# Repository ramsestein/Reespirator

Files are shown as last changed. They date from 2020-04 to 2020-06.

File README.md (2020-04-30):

# Reespirator 2020

Este repositorio pretende documentar y organizar los pasos para fabricar prototipos de  **Reespirator-2020**, un respirador open-source basado en el sistema de ventilación mecánica Jackson-Rees, diseñado y mejorado a partir de los prototipos elaborados por el equipo de Reesistencia Team para todas aquellas personas, organizaciones o empresas que quieran fabricarlo en cualquier parte del mundo.  

> ESTA DOCUMENTACIÓN ESTÁ EN ELABORACIÓN, COMPRUEBE REGULARMENTE LOS CAMBIOS, LAS PRIMERAS VERSIONES PUBLICADAS ESTÁN DESACTUALIZADAS. 

## Disclaimer
*Recuerde que un respirador es un dispositivo médico que sólo puede ser utilizado por personal cualificado y que un mal respirador o un respirador mal utilizado puede matar.*

La presente documentación **NO PERMITE CONSTRUIR UN RESPIRADOR FINAL**, sólo se publica para que se pueda fabricar PROTOTIPOS para investigación. 

## Info
*¿Qué es Reespirator 2020?*

El dispositivo Reespirator 2020 es un prototipo de sistema respirador de emergencia con elementos disponibles por la mayoría de las personas en cualquier parte del mundo, de rápida construcción y con la capacidad para mantener constantes ventilatorias aceptables en un paciente afecto de [Síndrome de Distrés Respiratorio Agudo](https://es.wikipedia.org/wiki/S%C3%ADndrome_de_dificultad_respiratoria_aguda) o SDRA que esperamos puede ser aplicable a los pacientes con COVID-19.

Aunque el origen de Reespirator es España, debido a las regulaciones y validaciones necesarias para los productos médicos, y aunque Reespirator 23 de [Reesistencia Team](https://gitlab.com/reesistencia), en el que se basó inicialmente este nuevo diseño, ha superado varias pruebas preclínicas con animales, y de compatibilidad electromagnética, suponemos que este dispositivo nunca se llegará a fabricar masivamente en España, dónde afortunadamente lo peor de la crisis del COVID-19 parece que ya ha pasado (08/04/20); esperamos que este y otros diseños puedan ser útiles en otros países.

Aún así no nos damos por vencidos y seguiremos desarrollando el proyecto al menos en 2 versiones:

* Versión low cost (basada en Arduino y con caja de metacrilato, madera...)
* Versión pro (con un autómata PLC + un HMI y caja de chapa plegada en acero inoxidable)

En la siguiente figura podemos ver una representación del dispositivo:

Reespirator

## Primeros pasos
**Antes de montar un respirador lea toda la documentación posible e infórmese bien, si necesita alguna aclaración abra un Issue y lo corregiremos en cuanto podamos. Si cree que puede mejorar el diseño, el código o que falta alguna cosa importante envíenos un Pull Request.**

## [Información médica básica del dispositivo Reespirator 2020](https://gitlab.com/reespirator/reespirator2020/-/blob/master/medical/MEDICAL.md)
El dispositivo se está diseñando para intentar cumplir las siguientes [especificaciones clínicas](https://foro.coronavirusmakers.org/index.php?p=/discussion/44/especificaciones-clinicas-de-un-respirador-util-en-esta-crisis#latest). Los dispositivos que estamos prototipando podrán funcionar en diferentes modos ventilatorios. En el siguiente enlace tendrás acceso a [Información médica básica sobre el dispositivo Reespirator 2020](https://gitlab.com/reespirator/reespirator2020/-/blob/master/medical/MEDICAL.md)

## [Estructura básica](https://gitlab.com/reespirator/reespirator2020/-/blob/master/case/CASE.md)
La versión low-cost de Reespirator 2020 consta de una [caja](https://gitlab.com/reespirator/reespirator2020/-/blob/master/case/CASE.md) diseñada para fabricarse mediante corte láser que contiene casi todos elementos del respirador en su interior. En el prototipo actual las piezas del prototipo se han diseñado para su corte por láser en metacrilato, si bien la imagen anterior corresponde a la nueva evolución que podrá fabricarse también con chapa plegada.

## [Sistema neumático](https://gitlab.com/reespirator/reespirator2020/-/blob/master/neumatic/NEUMATIC.md)
El [sistema neumático](https://gitlab.com/reespirator/reespirator2020/-/blob/master/neumatic/NEUMATIC.md) del Reespirator 2020 está basado en un sistema Jackson-Rees. Reespirator 2020 utiliza además una serie de válvulas, sensores de presión y caudal y tubuladuras para hacer llegar al aire a los pulmones del paciente.

## [Mecánica](https://gitlab.com/reespirator/reespirator2020/-/blob/master/mechanic/MECHANIC.md)
El [sistema mecánico](https://gitlab.com/reespirator/reespirator-doc/-/blob/master/mechanic/MECHANIC.md) pretende realizar los movimientos necesarios para realizar las maniobras de inspiración y espiración forzada del paciente mediante elementos mecánicos sustituyendo al personal humano que utilizaría el sistema de ventilación.

## [Electrónica](https://gitlab.com/reespirator/reespirator2020/-/blob/master/electronics/ELECTRONICS.md)
La [electrónica](https://gitlab.com/reespirator/reespirator-doc/-/blob/master/electronics/ELECTRONICS.md) de control gestiona el movimiento del motor y los sensores que permiten realizar un control de lazo cerrado automatizado del sistema.
Además de la electrónica de control se emplea una electrónica adicional como interfaz de usuario que permite monitorizar diferentes señales del respirador y modificar en tiempo real diferentes configuraciones del mismo.

## [Firmware](https://gitlab.com/reespirator/reespirator-doc/-/blob/master/firmware/FIRMWARE.md)
El sistema de control necesita ser programado con un [firmware](https://gitlab.com/reespirator/reespirator-doc/-/blob/master/firmware/FIRMWARE.md) que permita hacer funcionar el dispositivo. Dicho programa se ha realizado conforme a las especificaciones de los especialistas médicos para realizar las funciones para las que el dispositivo fue diseñado.

## [Simulación](https://gitlab.com/reespirator/reespirator2020/-/blob/master/simulation/SIMULATION.md)
En este apartado se consideran los fundamentos del sistema de control en lazo cerrado para los distintos modos de control que permite el Reespirator 2020. Los modelos matemáticos que permiten la [simulación numérica](https://gitlab.com/reespirasistemator/reespirator2020/-/blob/master/simulation/SIMULATION.md) del comportamiento del sistema corresponden a la información de este apartado.

## [Lista de materiales](https://gitlab.com/reespirator/reespirator2020/-/blob/master/bom/BOM.md)
La [lista de materiales, (BOM o Bill of materials)](https://gitlab.com/reespirator/reespirator2020/-/blob/master/bom/BOM.md) para construir un Reespirator 2020 es cuando menos complicada, incluye elementos como metacrilato, madera, MDF o chapa para la caja, sistmeas electrónicos como un Arduino Mega o un autómata PLC, y otros componentes, pero también elementos mecánicos y otros incluso impresos en 3D; pero sobre todo requiere también de la utilización de sistemas médicos tales como tubuladuras y un sistema ventilatorio Jackson-Rees.

## [Manual de usuario](https://gitlab.com/reespirator/reespirator2020/-/blob/master/manual/MANUAL.md)
El dispositivo Reespirator 2020 es un dispositivo médico y su uso sólo debe realizarse por personal especializado. Ofrecemos aquí un breve [manual de uso](https://gitlab.com/reespirator/reespirator-doc/-/blob/master/manual/MANUAL.md) del mismo; pero es el personal sanitario el que sabe los parámetros que deben utilizarse para el tratamiento de un paciente.

## [Vídeos]
En el siguiente enlace podemos ver algunos vídeos con detalles del Reespirator 2020 en funcionamiento:

* https://www.youtube.com/channel/UC9xr1HbWGLBjd4ADTvGcOnw

## Historia y principales cambios de esta versión

El proyecto Reespirator2020 toma como punto de partida el proyecto Reespirator 23 (o 24) v3 de **Reesistencia Team** a partir del cual realizamos un fork, el repositorio original está en [https://gitlab.com/reesistencia](https://gitlab.com/reesistencia).

En esta nueva versión se incluyen principalmente los siguientes cambios:

 - Revisión y reestructuración en profundidad del códido de Arduino para asegurar la robustez de funcionamiento en todos los supuestos.
 - La recuperación del interfaz básico con LCD de 20x04 y elementos sencillos de control (4 pulsadores y un encoder con pulsador).
 - Establecimiento y documentación de una interfaz de comunicación serie que permite la utilización de sistemas (en adelante llamados Display+) de visualización, control y conectividad, que pueden ser utilizados como accesorios para aportar mejor usabilidad al sistema.
 - Se trabaja para estandarizar y popularizar los sensores y electro-válvulas para utilizar partes (comerciales o diseñadas) posibles de conseguir con la situación de emergencia actual y a precios accesibles.
 - Posibilidad de usar diferentes interfaces de usuario.
 - Opción de utilizar un microcontrolador tipo Arduino o similar o bien un autómata PLC.

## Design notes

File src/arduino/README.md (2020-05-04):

# Arduino

> Estamos elaborando una nueva versión para Arduino más sólida a partir de la versión del software que se ha hecho para el PLC. En las carpetas https://gitlab.com/reespirator/firmware y https://gitlab.com/reespirator/display están las versiones de los desarrollos actuales de Reespirator 2020.

## Reespirator 23

En el repositorio https://gitlab.com/reesistencia/reespirator está el código de la versión utilizada originalmente en Reespirator 23 para Arduino y la Beagle Bone con una pantalla táctil de 7" de WaveShare.

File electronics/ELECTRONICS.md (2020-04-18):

## Electrónica
La electrónica de control gestiona el movimiento del motor y los sensores que permiten realizar un control de lazo cerrado automatizado del sistema. Además se emplea una electrónica adicional de interfaz de usuario que permite monitorizar diferentes señales del respirador y modificar en tiempo real diferentes configuraciones del mismo.

* En la versión de [Arduino](https://gitlab.com/reespirator/reespirator2020/-/blob/master/electronics/arduino/ARDUINO-ELECTRONICS.md) la electrónica de control está basada en un Arduino Mega y una serie de dispositivos sensores y actuadores conectados al mismo para realizar un sistema de control en lazo cerrado. 

* Estamos trabajando también en una versión basada en un autómata o [PLC](https://gitlab.com/reespirator/reespirator2020/-/blob/master/electronics/PLC/PLC-ELECTRONICS.md) que fundamentalmente ha permitido realizar una correcta modelización del sistema.

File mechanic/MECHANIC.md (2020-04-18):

El sistema mecánico de Reespirator utiliza un motor Nema 23/24 que hace oscilar una leva con forma de caracol y esta mueve a su vez una palanca que bascula haciendo moverse al empujador que aprieta sobre el globo del Jackson-Rees.

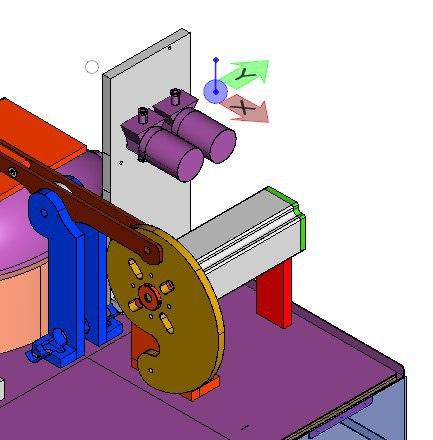
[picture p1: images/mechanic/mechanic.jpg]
Detalle Detalle de la leva, el motor y la palanca


La parte mecánica consta de:

* Una leva fabricada en metacrilato de 8mm. con un casquillo adaptador, fabricado en acero o aluminio.

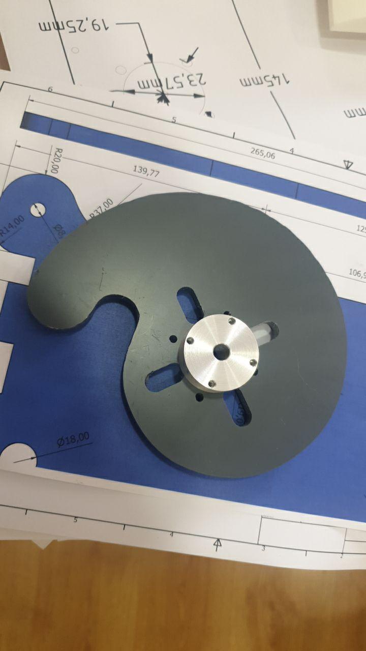
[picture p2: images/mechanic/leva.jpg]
Leva Leva cortada en madera


* Un balancín formado por 2 piezas de metacrilato de 4 mm. Dispone de un rodamiento 608ZZ, que entra en contacto con la leva y pivota sobre un tornillo M8 que lo ancla a la estructura de la caja, y en su parte final está fijado a una pala, impresa en 3D, con dos tornillos M5.

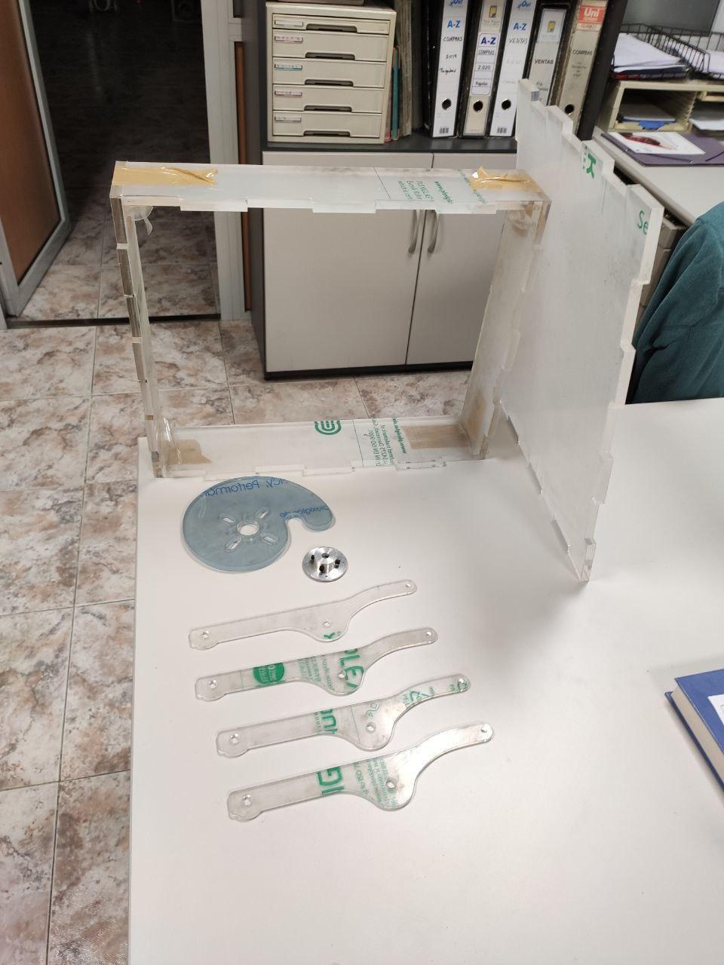
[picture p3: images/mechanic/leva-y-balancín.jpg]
Piezas del balancín y la leva Piezas del balancín y la leva cortadas en metacrilato


* La carcasa, que contiene todo el dispositivo está fabricada en metacrilato de 10mm, dispone además de un embellecedor, cortado en láser de metacrilato de 4mm para protección mecánica.

Caja cortada por láser

* Además, dispone de una [cuna](https://gitlab.com/reespirator/reespirator2020/-/blob/master/files/stl/cuna.stl "Cuna impresa en 3D para alojar el balón del Jackson-Rees") impresa en 3D donde se aloja el balón respirador de Jackson Rees.

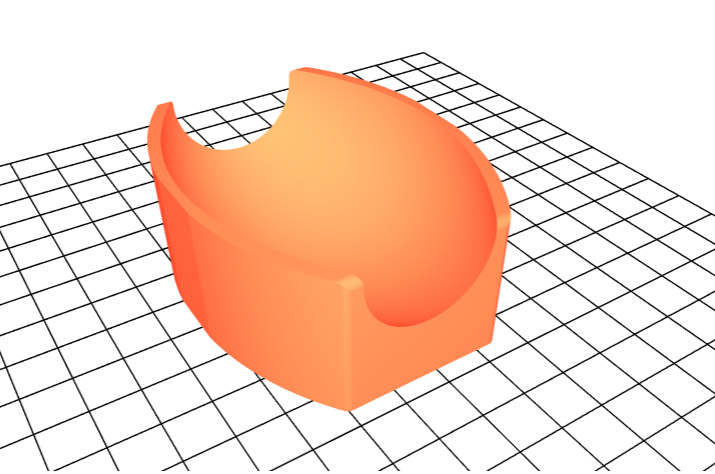
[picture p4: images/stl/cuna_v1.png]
Cuna para el Jackson-Rees


* El sistema utiiza también una [pala o empujador](https://gitlab.com/reespirator/reespirator2020/-/blob/master/files/stl/empujador_v3.stl "Cuna impresa en 3D para alojar el balón del Jackson-Rees") impresa en 3D que empuja el balón respirador para insuflar el aire al paciente. 

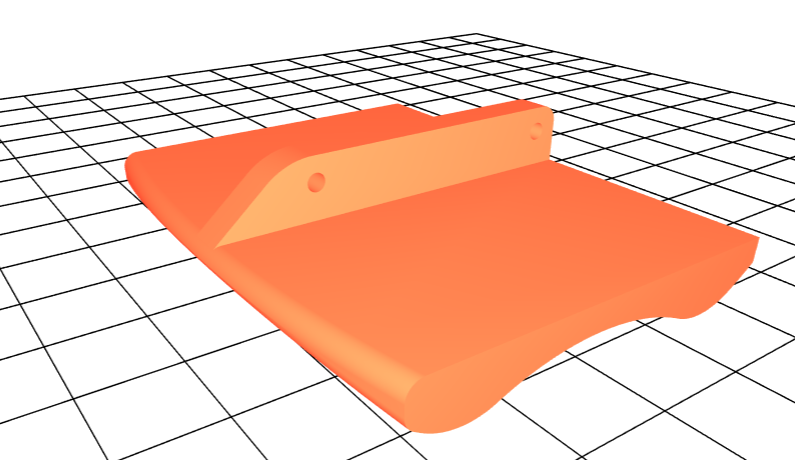
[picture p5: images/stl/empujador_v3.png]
Pala o empujador


*Estas 2 piezas se imprimirán en 3D con la mayor calidad posible, pues ambas quedan en contacto con el globo y no deben tener fallos que puedan dañar el mismo.*

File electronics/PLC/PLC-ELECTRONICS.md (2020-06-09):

***Este documento describe la electrónica basada en PLC. Si desea ver la versión para Arduino, está disponible en el siguiente enlace: https://gitlab.com/reespirator/reespirator2020/-/blob/master/ARDUINO-ELECTRONICS.md***

## Electrónica con PLC 
La electrónica de control gestiona el movimiento del motor y los sensores que permiten realizar un control de lazo cerrado automatizado del sistema. Además se emplea una electrónica adicional de interfaz de usuario que permite monitorizar diferentes señales del respirador y modificar en tiempo real diferentes configuraciones del mismo.

El diagrama de bloques funcionales y elementos electrónicos del sistema se muestra en la siguiente figura:
_PENDIENTE_

### PLC

Según este esquema podemos ver que el sistema electrónico está compuesto por un autómata SIEMENS Simatic S7-1200 CPU 1215c al que se conectan los sensores y actuadores del sistema. Opcionalmente se puede suministrar la misma CPU en su versión SAFETY CAT-IV/SIL 3 mejorando grandemente tiempo medio entre fallos (mtbf), que ya de por si es bajo.

SIEMENS Simatic S7-1200

### Display táctil

Dispone de un display táctil SIEMENS TP700, con las siguientes capacidades: registro de alarmas, histórico de datos, monitorización remota con gestión de usuario y password para evitar accionamientos no autorizados. El gestor de accesos indica en la pantalla si se está operando sobre la pantalla en remoto. Dispone de una memoria SD para almacenamiento de datos de alarmas y datos de trabajo.

SIEMENS TP700

### Etapa de alimentación:
El dispositivo está preparado para conectarse a la red eléctrica de 110-230V de corriente alterna y utiliza una fuente de alimentación principal de baja tensión de 24V de corriente continua capaz de suministrar al menos 15A. Para mantener su funcionamiento en caso de fallo de la alimentación debe emplearse un SAI o bien solicitar alimentación auxiliar de 24Vdc.

### Sistema de actuación y sensorización

* Se utilizarán motores NEMA, concretamente NEMA 24 que si bien no son tan comunes como los NEMA 23 dan un torque suficiente. En los prototipos hemos utilizado motores de 4,2N/m. En cualquier caso el uso de otro tipo de motores debe garantizar la suficiente presión sobre el globo del Jackson-Rees para producir el suficiente flujo ventilatorio.

Nema 24 Motor Nema 24

* Los motores NEMA se controlarán con un driver HSS57. Se ha elegido este modelo ya que puede controlar tanto el NEMA24 como motores más pequeños sin necesidad de cambiar todo el hardware.
En el repositorio está publicado también el driver para este modelo.

Esquema de conexión Esquema de conexión del driver y el motor paso a paso

* Para monitorizar la posición inicial del sistema, se utilizará un sensor de efecto hall o un simple final de carrera, (aunque también se ha considerado la opción de un segundo sensor para evitar problemas).

* Electroválvula de 24V para el control de salida de aire del sistema neumático, (en el prototipo original se utilizaron 2 porque eran de un diámetro demasiado pequeño como para permitir un caudal apropiado).

* Sensor de caudal Sensirion SFM3300-AW para la medición del caudal en el espacio muerto del sistema de ventilación. Al ser una pieza que estará en contacto con el circuito de inspiración del paciente, se emplea un sensor homologado para aplicaciones médicas. (Si este modelo no estuviera disponible se pueden buscar sustitutos y con pequeñas modificaciones del código se podrían utilizar igualmente).

Caudalímetro

* Sensor de presión diferencial para la diferencia de presión que existe entre el circuito inspiratorio y la presión ambiental. Se ha empleado el modelo ABPLANT001PG2A5 de Honeywell, que está homologado para aplicaciones médicas. (En versiones previas utilizamos 2 BME280 conectados por SPI).

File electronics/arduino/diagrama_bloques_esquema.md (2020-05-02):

## Diagrama Bloques Placa Electrónica Principal ##

La electrónica principal para la versión de Arduino se basa en el desarrollo de una placa PCB de doble cara diseñada para montaje SMD. Esta placa contendrá los elementos necesarios para asegurar la protección ESD así como los distintos elementos para el control de los sensores, actuadores y comunicación con el exterior.

Para aclarar cada una de las partes de las que consta esta placa, se desglosará el esquemático en los siguientes bloques que se exponen a continuación, (en los enlaces siguientes encontrarás más información):

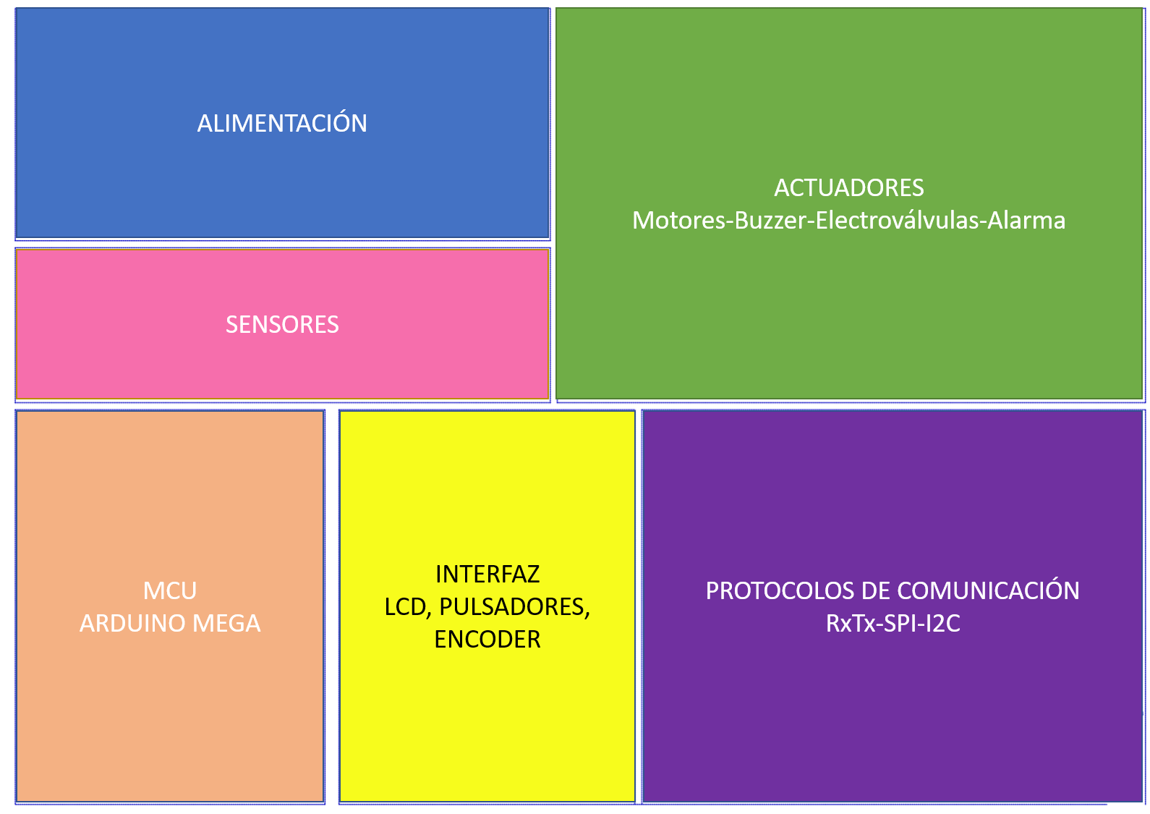
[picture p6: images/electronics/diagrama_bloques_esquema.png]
Diagrama Bloques Esquema Electrónico Diagrama de Bloques de la Electrónica


[- Alimentación.](https://gitlab.com/reespirator/reespirator2020/-/blob/master/electronics/arduino/alimentacion_esquema.md "Alimentacion Esquema")

[- Actuadores: Motores, buzzer, electroválvulas, alarma.](https://gitlab.com/reespirator/reespirator2020/-/blob/master/electronics/arduino/actuadores_esquema.md "Actuadores")

[- Sensores.](https://gitlab.com/reespirator/reespirator2020/-/blob/master/electronics/arduino/sensores_esquema.md "Sensores")

[- Interfaz: LCD, encoder, pulsadores.](https://gitlab.com/reespirator/reespirator2020/-/blob/master/electronics/arduino/interfaz_esquema.md "Interfaz")

[- Protocolos de comunicación: SPI, I2C, TxRx.](https://gitlab.com/reespirator/reespirator2020/-/blob/master/electronics/arduino/comunicacion_esquema.md "Protocolos de Comunicación")

[- MCU: Arduino Mega.](https://gitlab.com/reespirator/reespirator2020/-/blob/master/electronics/arduino/mcu_esquema.md "MCU Conexiones")

## Representación Tridimensional de la PCB ##

Como resultado de este trabajo se obtiene la siguiente PCB en la que se pude ver una representación tridimensinal:

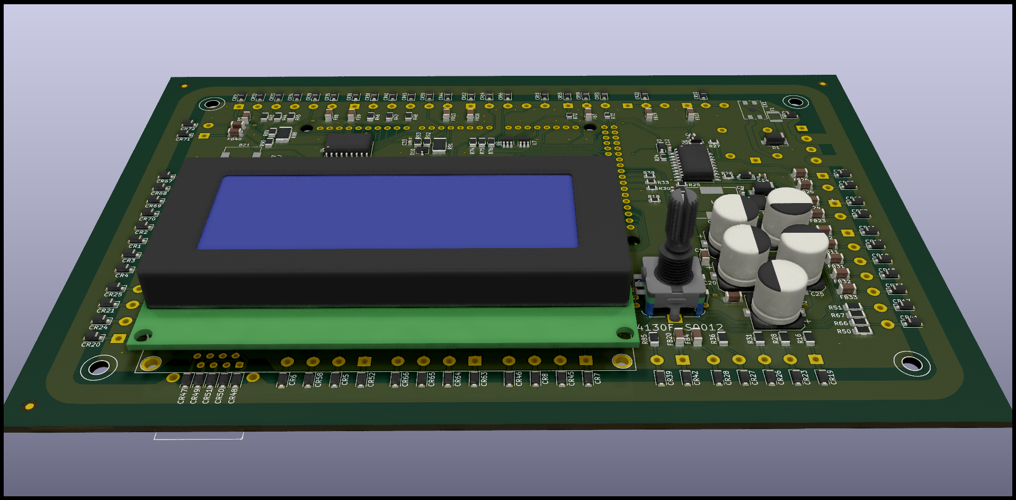
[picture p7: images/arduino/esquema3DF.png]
Representación 3D Parte Superior Representación 3D de la Electrónica. Parte superior


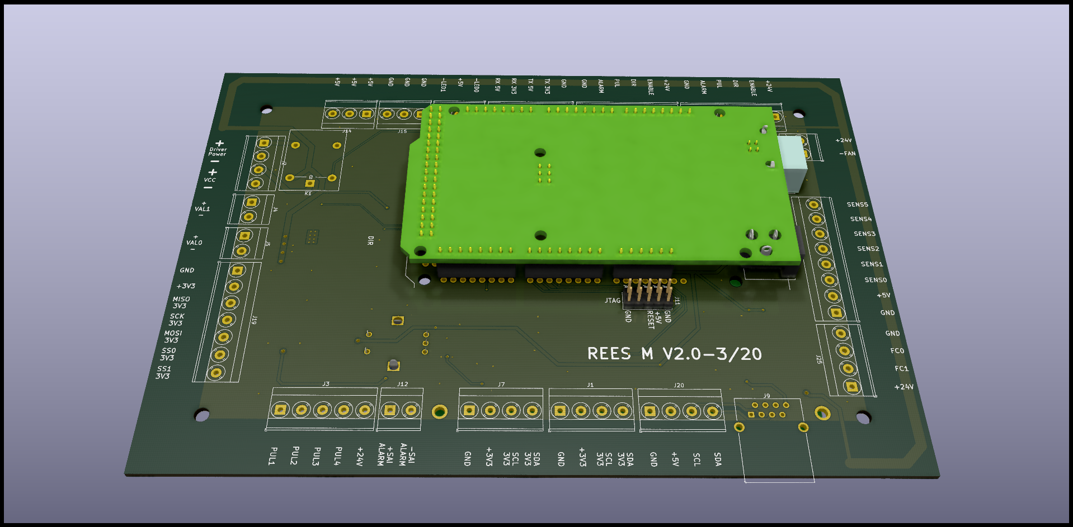
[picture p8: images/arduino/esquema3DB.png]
Representación 3D Parte Inferior Representación 3D de la Electrónica. Parte Inferior


## Diseño PCB ##

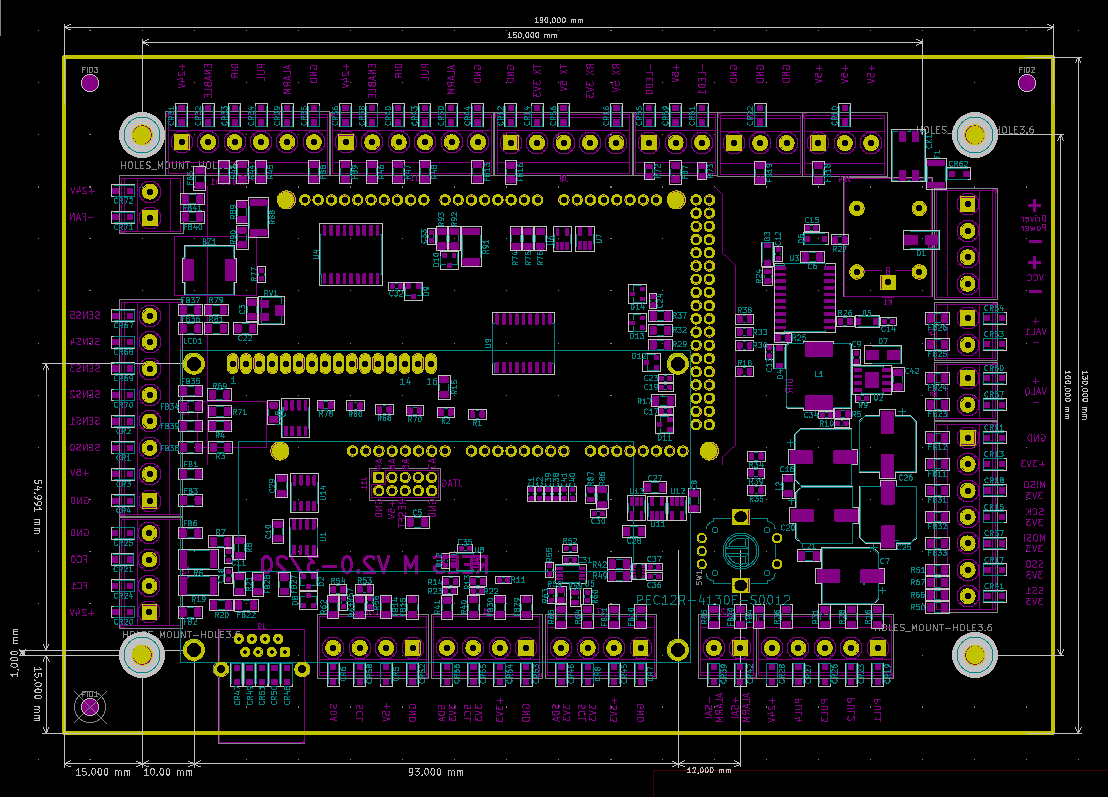
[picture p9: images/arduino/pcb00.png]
Diseño PCB Representación de pads


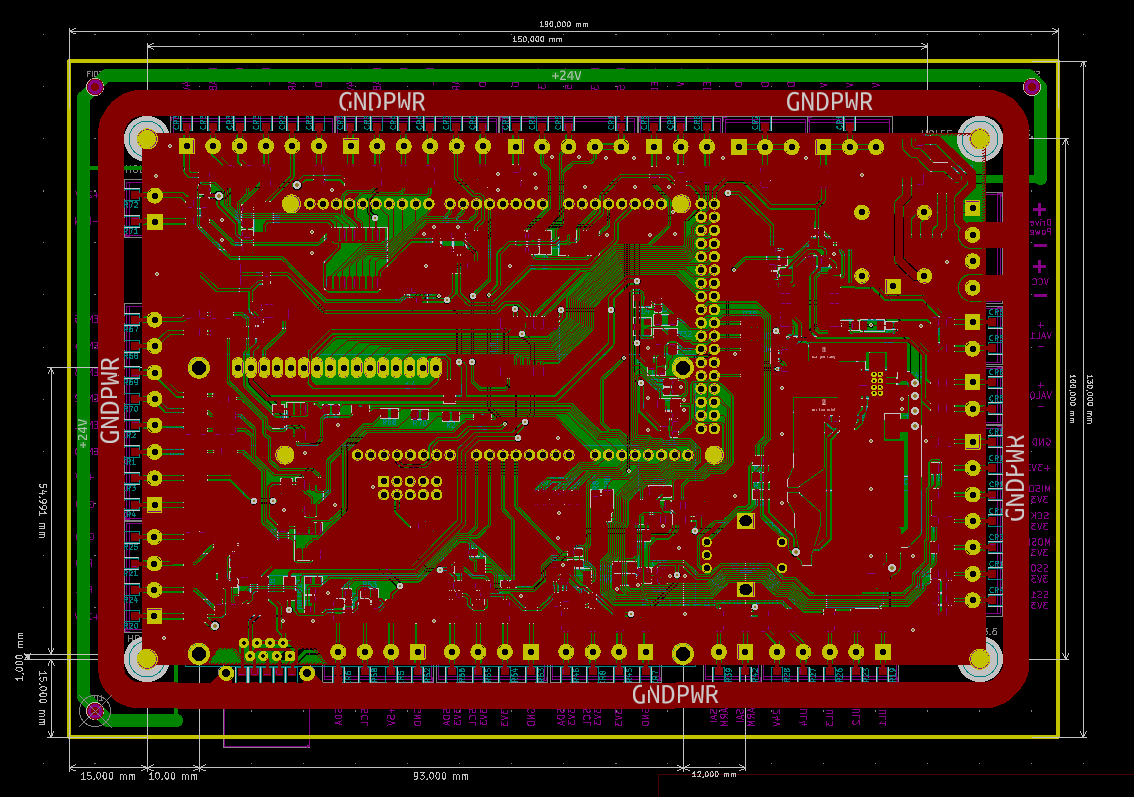
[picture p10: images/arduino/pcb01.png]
Diseño PCB PCB Completa


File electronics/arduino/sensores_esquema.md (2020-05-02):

El diagrama de bloques de la placa de circuito impreso diseñada para la versión del arduino, está disponible en el siguiente enlace:

**[Diagrama de Bloques](https://gitlab.com/reespirator/reespirator2020/-/blob/master/electronics/arduino/diagrama_bloques_esquema.md "Diagrama de Bloques")**

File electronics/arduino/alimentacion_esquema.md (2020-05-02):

## Fuente de Alimentación. ##

Para la alimentación el sistema se empleará una fuente de alimentación capaz de suministrar un mínimo de 3A y con salida de 24V.

De entre todas las fuentes del mercado, lo recomendable sería emplear una fuente que haya sido diseñada para emplearse en equipos médicos puesto que dispondrá de circuitos específicos para el aislamiento ante posibles interferencias (EMI).

Preferiblemente se optará por una fuente de alimentación conmutada que permite entre otras cosas disponer de una fuente de alimentación menos voluminosa con un mayor rendimiento.

Un posible diagrama de bloques de la fuente de alimentación seleccionada es la que se presenta en la figura siguiente:

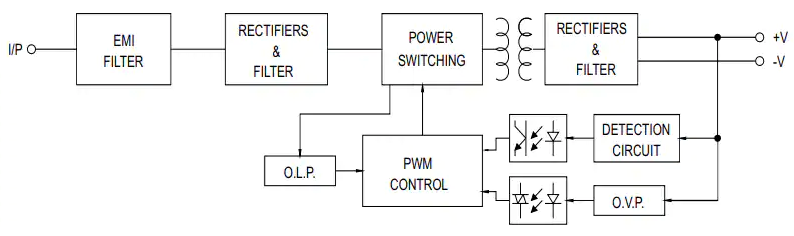
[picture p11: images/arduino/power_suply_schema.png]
Diagrama Bloques Fuente Alimentación


Existen muchas alternativas en el mercado, por lo que atendiendo a la disponibilidad y coste, se podrá optar por una u otra. Dicha fuente es la que alimentará entre otras partes del sistema a la placa de circuito impreso que se ha desarrollado. 

## Esquema del circuito electrónico de alimentación. ##

Como se podrá observar, esta parte del circuito corresponde a la alimentación de los distintos componentes y al sistema en general. Cabe destacar que se parte de una fuente de alimentación de +24V en corriente continua como se ha indicado anteriormente.

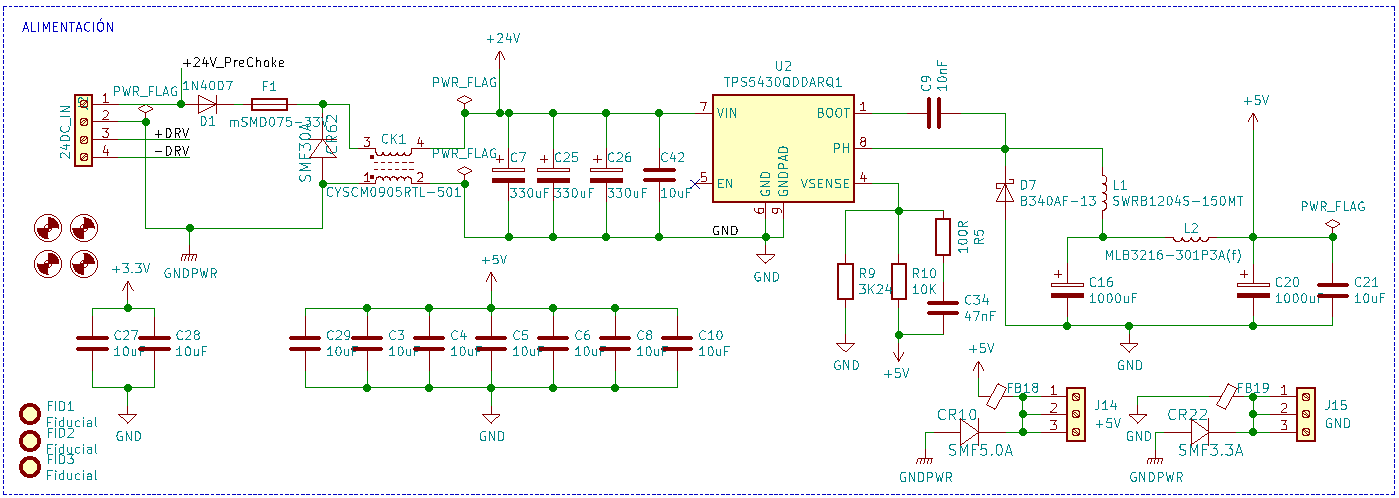
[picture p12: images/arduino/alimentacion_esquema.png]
Esquema Fuente Alimentación


En el esquema se puede observar cómo de los bornes de entrada de la fuente de alimentación de 24V tenemos 4 salidas, las dos primeras son las que proporcionarán tensión y corriente a toda la placa, mientras que las dos inferiores son las que proporcionarán tensión al DRV.

La alimentación pasa a través de F1 que servirá de fusible para proteger el sistema y tras él se encuentra un Choke para evitar las interferencias y proteger de EMI. Tras el Choke CK1, se pueden distingir dos apartados:

- El primero de ellos es una **salida de +24V**. Esta salida se empleará en la parte de actuadores como drivers, válvulas..etc., como se verá más adelante.
- La segunda es una **salida de 5V** que se obtiene tras pasar un convertidor DC/DC con capacidad para conducir 3A. 

Todo esto permite tener una alimentación estable en la placa de +24V y +5V, protegida por diferentes componentes como ferritas y diodos de protección.

En esta parte también se puede ver una red de condensadores que son de desacoplo y que estarán ubicados lo más próximos posible a la alimentación de los circuitos integrados. 
Y por último también se pueden observar algunos de los conectores  de alimentación, que estarán disponibles para conectar periféricos, todos ellos protegidos por diodos unidireccionales TVS (Transient Voltage Suppressors).

El diagrama de bloques de la placa de circuito impreso diseñada para la versión del arduino, está disponible en el siguiente enlace:

**[Diagrama de Bloques](https://gitlab.com/reespirator/reespirator2020/-/blob/master/electronics/arduino/diagrama_bloques_esquema.md "Diagrama de Bloques")**

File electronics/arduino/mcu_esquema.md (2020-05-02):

## MCU Esquema. ##

Como se ha comentado en varias ocasiones, esta versión del respirador está basada en un Arduino Mega 2560.
Este microcontrolador será el encargado de llevar a cabo el control y gestión del sistema, sin embargo, dependiendo de la versión de la interfaz escogida, podrá relegar el control de la visualización a otro sistema a parte que permita la representación gráfica.

En cualquier caso, la placa desarrollada dispone de varias opciones de visualización tal y como se ha detallado en la documentación, en el apartado: [Interfaz](https://gitlab.com/reespirator/reespirator2020/-/blob/master/electronics/arduino/interfaz_esquema.md "Interfaz") 

En la siguiente imagen se puede ver el esquema de conexión empleado en el sistema.

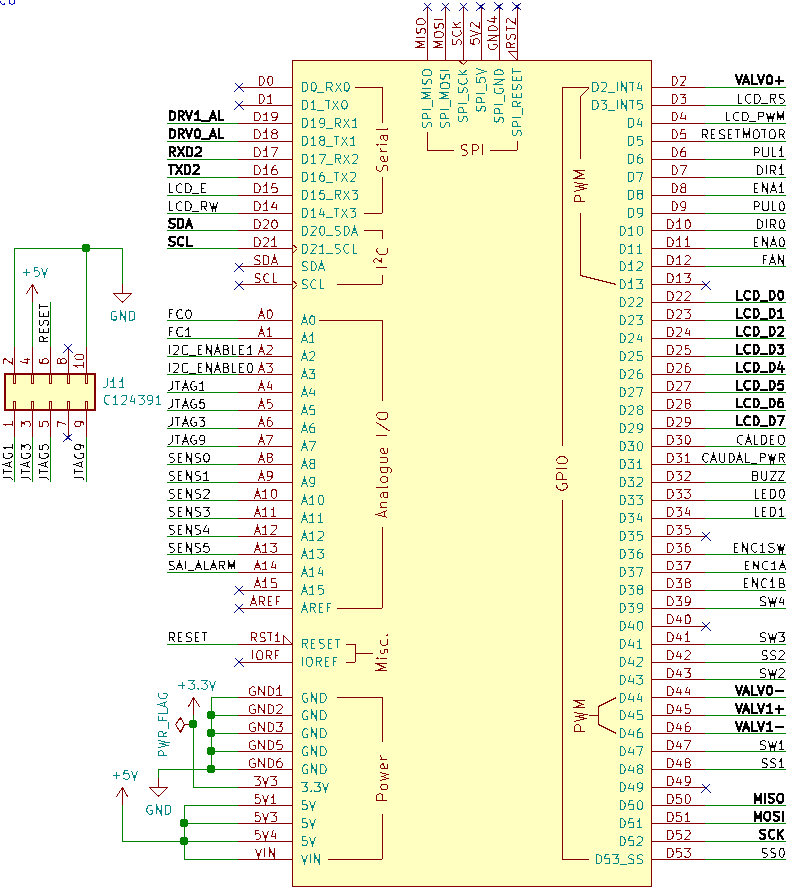
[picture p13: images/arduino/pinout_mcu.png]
MCU


Como se puede apreciar en la imagen, se dispone por un lado del microcontrolador con su pinout, donde se han señalado en **negrita**, aquellos pines fijos que no podían reubicarse en el diseño de la pcb, y por otro lado, existe un bloque denominado J11 consistente en un conector para facilitar la depuración del sistema mediante JTAG.

A partir del microcontrolador, se tiene toda la información proveniente de sensores y por lo tanto permitirá actuar sobre los distintos elementos como alarma, buzzer, válvulas..etc.

El diagrama de bloques de la placa de circuito impreso diseñada para la versión del arduino, está disponible en el siguiente enlace:

**[Diagrama de Bloques](https://gitlab.com/reespirator/reespirator2020/-/blob/master/electronics/arduino/diagrama_bloques_esquema.md "Diagrama de Bloques")**

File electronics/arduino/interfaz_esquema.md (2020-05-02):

## Interfaz del Sistema. ##

La interacción del usuario con el sistema se realizará a través de una serie de pulsadores y un encoder, además de un display, la ubicación de estos elementos estará debajo de un LCD 4x20 y a la derecha del mismo respectivamente.

Como se indicó en la introducción a la electrónica del respirador, este dispositivo **se ha pensado para tener distintas opciones de montaje y funcionamiento**, siendo la que se detalla a continuación la básica de ellas, pero no la única, puesto que **el sistema está preparado para la conexión a través de los terminales de TxRx y/o del USB**, para la comunicación con otros periféricos de visualización como puede ser una pantalla oled o HMI. 

**La selección de una forma de representación u otra se realizará vía firmware** por lo que no es necesario realizar ningún acople o adaptación a la placa desarrollada, simplemente se seleccionará el dispositivo de visualización deseado o instalado en el equipo en el firmware que se programa en el Arduino Mega.

**Esta versión de LCD 4x20, fue la primera versión que se pensó debido a su bajo coste y a la facilidad para disponer de estas en cualquier parte del mundo**, sin embargo, su limitación a la hora de representar señales y/o gráficas ha hecho necesario adaptar el sistema a otro tipo de dispositivos.

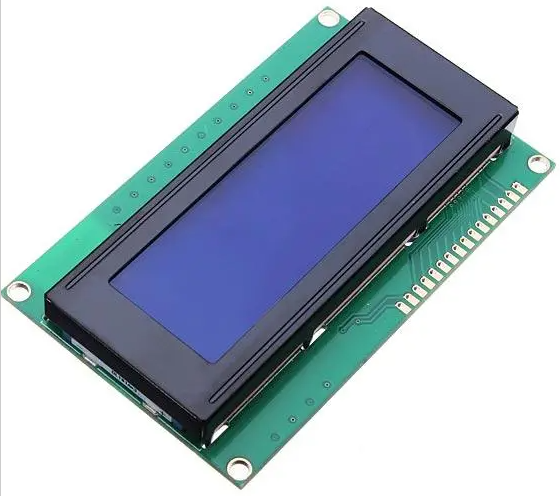
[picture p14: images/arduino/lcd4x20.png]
LCD 4x20 LCD 4X20


En la siguiente imagen se puede ver el esquema de esta parte del sistema.

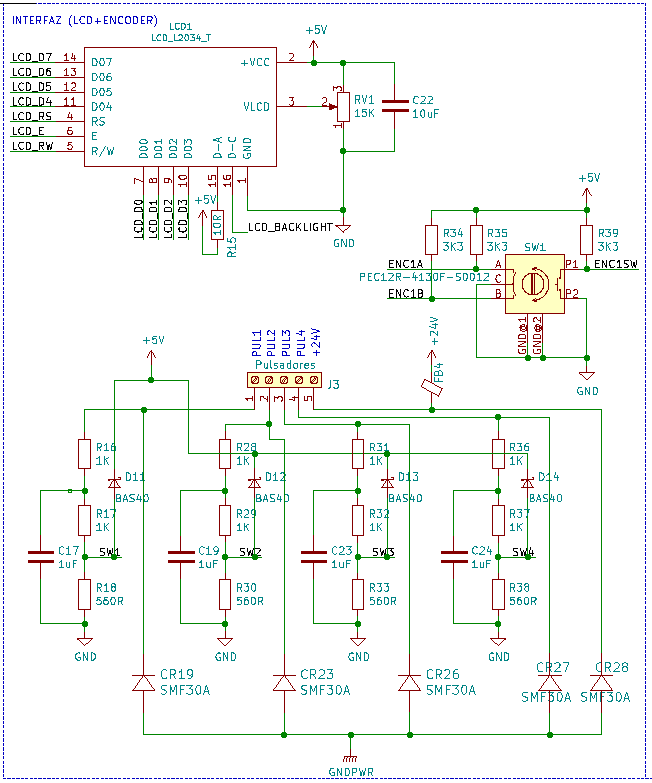
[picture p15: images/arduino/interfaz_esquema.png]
Esquema de la Interfaz


Como se puede comprobar, se dispone de un LCD con backlight el cual se encuentra conectado en paralelo con el Arduino Mega, disponiendo de un potenciómetro para regular el contraste.

En cuanto a los pulsadores, se dispone de 4 pulsadores que irán cableados a la borna de la placa, estos pulsadores conectados a 24V. Para evitar rebotes y sobretensiones en el Arduino, se ha protegido esta parte del sistema mediante condensadores y **diodos BAS40**, que impedirán que el Arduino encuentre sobretensión en las patillas destinadas al control de los pulsadores. También se han acoplado **diodos unidireccionales TVS** (Transient Voltage Suppressors) para la protección en la tensión de 24V.
 
Por último, esta parte dispone de un **enconder rotatorio con switch**, el cual permitirá hacer selección de configuraciones por parte del usuario de una forma sencilla. 

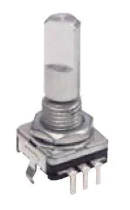
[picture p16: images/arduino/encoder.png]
Encoder


El diagrama de bloques de la placa de circuito impreso diseñada para la versión del arduino, está disponible en el siguiente enlace:

**[Diagrama de Bloques](https://gitlab.com/reespirator/reespirator2020/-/blob/master/electronics/arduino/diagrama_bloques_esquema.md "Diagrama de Bloques")**

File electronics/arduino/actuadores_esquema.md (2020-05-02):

## ACTUADORES Esquema. ##

En esta parte del esquema electrónico se verán los distintos componentes empleados para actuar sobre el sistema.

En la siguiente imagen se puede observar el diseño de lo mencionado:

[Esquema Actuadores](https://gitlab.com/reespirator/reespirator2020/-/raw/master/images/arduino/actuadores_esquema.png "Actuadores") 

Como se puede observar, el primero de los integrados que se observa es el **ULN2803A**, este circuito integrado, está compuesto por un conjunto de ocho puertas inversoras implementadas con transistores NPN tipo Darlington, lo que le permite soportar la conexión de dispositivos que requieren una fuerte demanda de corriente como motores paso a paso o relés que se podrán activar con una baja corriente de entrada.

ULN2803

De este modo, están conectados a sus entradas las señales de control del microcontrolador, y las salidas irán a los dispositivos mencionados como son el FAN (Ventilador), los drivers de los motores..etc. Tal y como se ha mencionado en otros apartados, estas salidas están protegidas mediante diodos TVS unidireccionales (SMF30).

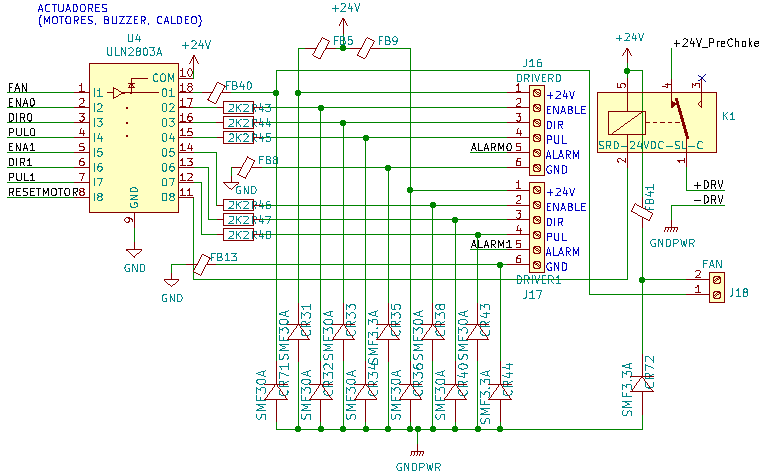
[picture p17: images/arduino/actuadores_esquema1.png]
Esquema Actuadores Actuadores

 
Debido al elevado número de dispositivos a controlar es necesario disponer de dos de estos circuitos integrados, empleando el segundo de ellos para controlar el Buzzer, el backlight de la pantalla LCD, el caldeo (heater) del caudalímetro, así como el control de 2 diodos led que se han añadido para posibles indicaciones.

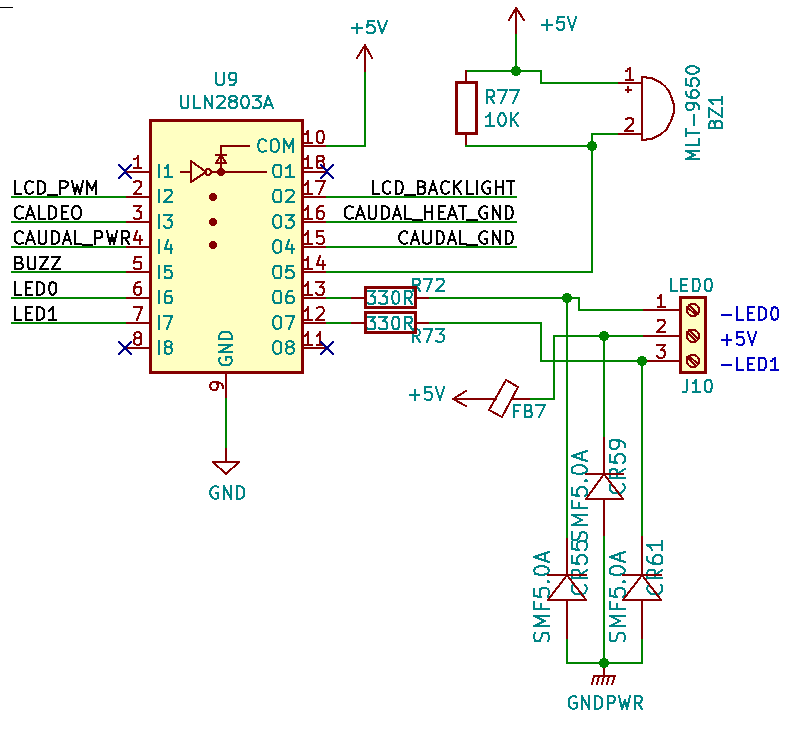
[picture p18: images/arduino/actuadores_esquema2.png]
Esquema Actuadores Actuadores


También se ha tenido en cuenta en esta parte una alarma para el **SAI** (Sistema de Alimentación Ininterrumpida), de forma que el sistema tenga control sobre cuál es la alimentación con la que se está funcionando.

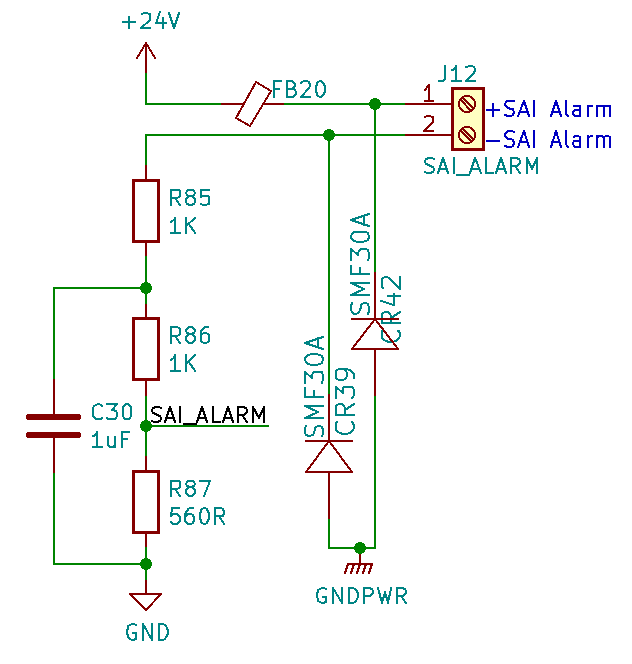
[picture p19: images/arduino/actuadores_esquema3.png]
Esquema Actuadores Actuadores


Por último, estaría el control de las electroválvulas, en este caso se pueden controlar 2 electroválvulas. El control de éstas se realiza a través de la conexión del microcontrolador al circuito integrado **L293**, el integrado L293D incluye dos circuitos puente H, para controlar cargas como motores o en el caso que nos ocupa electroválvulas:

L293

La salida del L293, que irá conectada a las electroválvulas está protegida una vez más mediante ferritas y diodos TVS unidireccionales, 

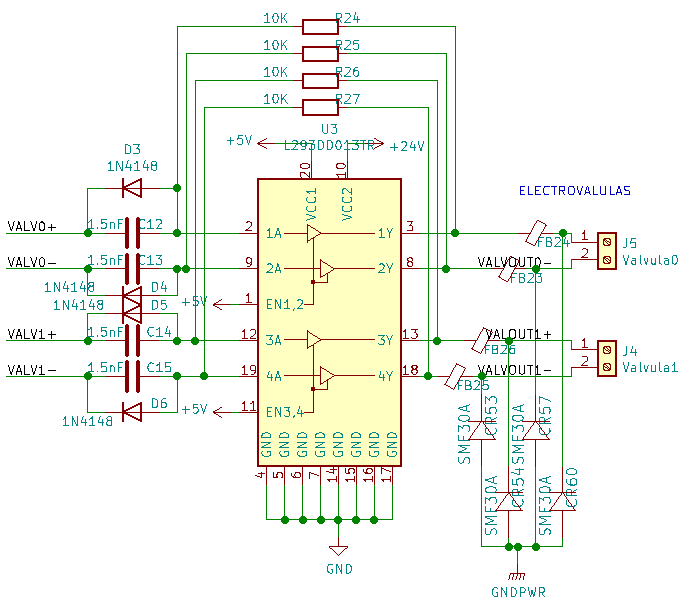
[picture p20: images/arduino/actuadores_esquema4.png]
Esquema Actuadores Actuadores


El diagrama de bloques de la placa de circuito impreso diseñada para la versión del arduino, está disponible en el siguiente enlace:

**[Diagrama de Bloques](https://gitlab.com/reespirator/reespirator2020/-/blob/master/electronics/arduino/diagrama_bloques_esquema.md "Diagrama de Bloques")**

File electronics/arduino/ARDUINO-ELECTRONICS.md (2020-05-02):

***Este documento describe la electrónica basada en Arduino. Si desea ver la versión para PLC, está disponible en el siguiente enlace: https://gitlab.com/reespirator/reespirator2020/-/blob/master/PLC-ELECTRONICS.md***

## Electrónica basada en Arduino
La electrónica de control gestiona el movimiento del motor y los sensores que permiten realizar un control de lazo cerrado automatizado del sistema. Además se emplea una electrónica adicional de interfaz de usuario que permite monitorizar diferentes señales del respirador y modificar en tiempo real diferentes configuraciones del mismo.

* En la versión de Arduino la electrónica de control está basada en un Arduino Mega y una serie de dispositivos sensores y actuadores conectados al mismo para realizar un sistema de control en lazo cerrado. 

* Estamos trabajando también en una versión basada en un autómata o PLC que fundamentalmente ha permitido realizar una correcta modelización del sistema.

En el prototipo actual la conexión de los distintos elementos se ha realizado sobre una shield de prototipado o breakout pero se está diseñando también una shield específica con los elementos necesarios para un ensamblado rápido de toda la electrónica, de forma que sólo sea necesario conectar los elementos sensores y actuadores mediante conectores.

Actualmente, se está trabajando el diseño de un PCB específico que integre la diversa electrónica que, en el prototipo, se ha realizado mediante módulos externos. Este desarrollo se irá liberando en el repositorio https://gitlab.com/reesistencia/reespirator-hardware

## Diagrama de Bloques del Sistema ##
En la siguiente figura se muestra de forma genérica el diagrama de bloques funcionales y elementos electrónicos del sistema:
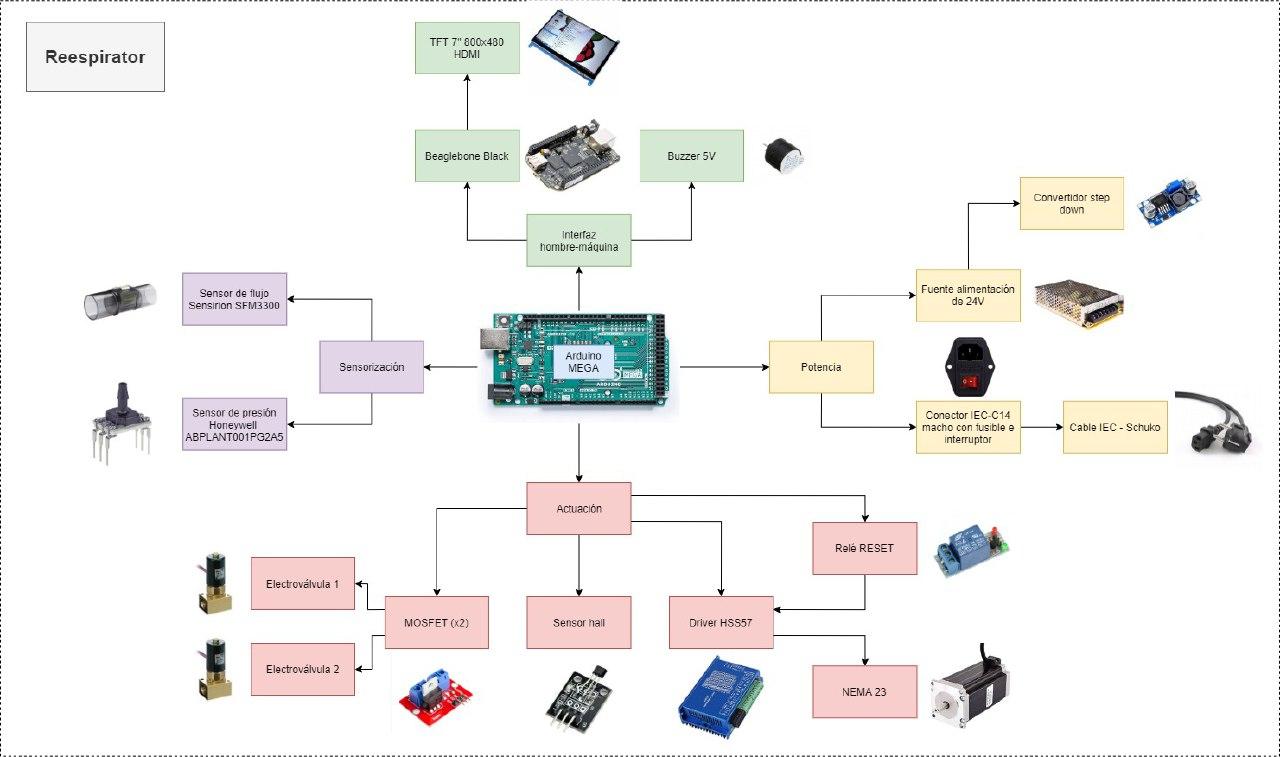
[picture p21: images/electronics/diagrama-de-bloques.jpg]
Diagrama de bloques


Según este esquema se puede observar que el sistema electrónico está compuesto por los siguientes bloques:

## Microcontrolador: 
Se ha empleado un Arduino Mega 2560 Rev3
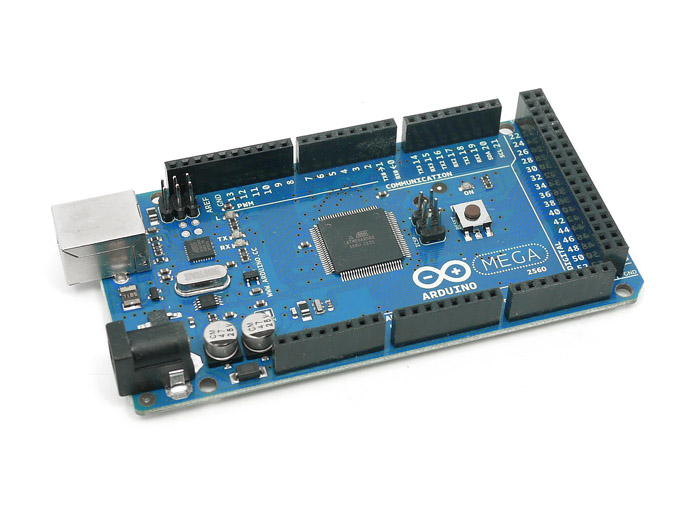
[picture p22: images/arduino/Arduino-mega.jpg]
Arduino Mega


## Etapa de alimentación:
Encargada de suministrar la energía necesaria para que todo el equipo funcione, está formada por los siguientes elementos:
	* La conexión a la red eléctrica se realizará mediante un conector IEC-C14 con fusible e interruptor.
	* La fuente de alimentación con entrada de 115-220V de corriente alterna de 50Hz/60Hz y salida 24Vdc.
	* Regulador step-down con salida de 5Vdc.
	
{Insertar esquema de conexión}

## Interfaz hombre-máquina: 
Permite la interacción entre el sistema y el usuario, mostrando la información necesaria o permitiendo actuar sobre los parámetros configurables. Para llevar a cabo esta tarea, la electrónica se ha diseñado para ofrecer dos formas principales de interacción con el usuario y que se describen a continuación: 
1. Interfaz de usuario básica: esta interfaz de usuario es la que se encuentra integrada en el diseño de la placa de la electrónica principal y que permitiría visualizar los parámetros básicos en un display sencillo (LCD 20x4), así como interactuar con el sistema.
2. Interfaz de usuario adicional, también denominada *Display+*: esta interfaz ajena a la placa principal, se comunicará con ésta para mostrar las gráficas o datos del sistema, de modo que el usuario final puede disponer de una interfaz de representación o visualización más completa. 

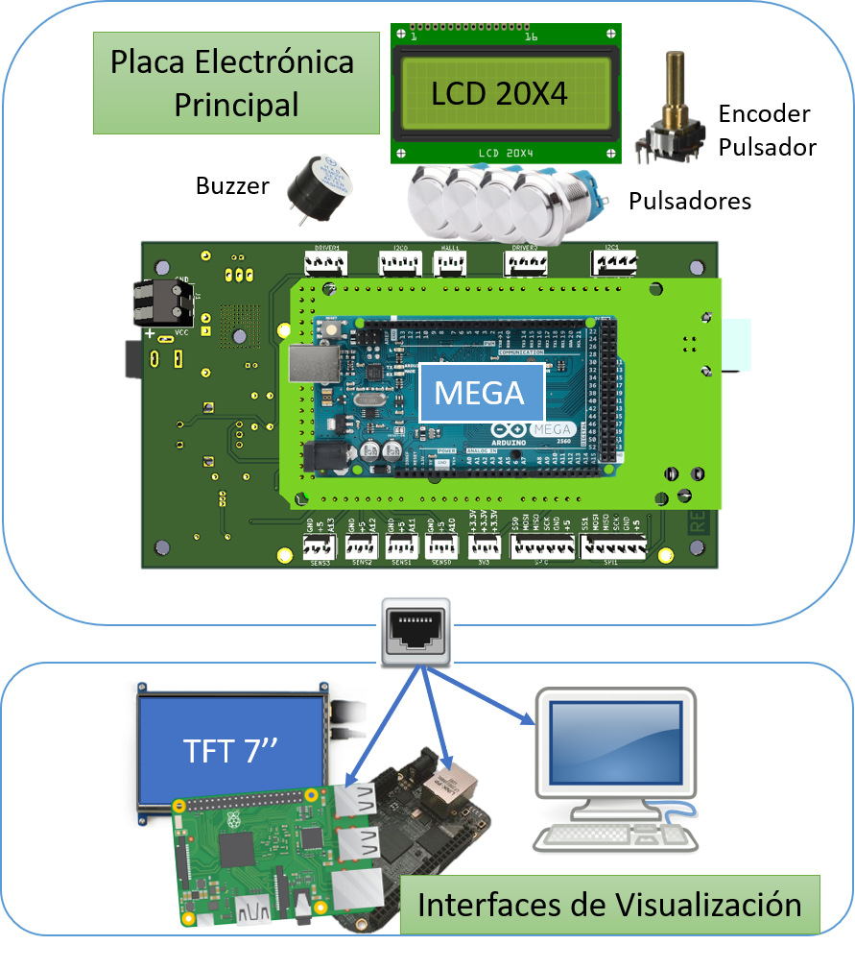
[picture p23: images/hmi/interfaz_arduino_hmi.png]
Posibles Interfaces


Un ejemplo de este último sistema es con el que se han realizado las pruebas y que ha estado constituido por los siguientes elementos.

* PC embebido BeagleBone Black, que dispone de un procesador AM325x 1GHz Cortex A8, con 4GB de memoria flash y 512MB de memoria RAM DDR3.
* Pantalla TFT táctil de 7 pulgadas, con conexión HDMI, del fabricante ShareWave y resolución 800x480.
* Para la señalización de alarmas, se dispondrá de un zumbador acústico activo.

**Se insiste en que este es el sistema utilizado en el prototipo; pero se podría plantear la utilización de otros, aunque caso de ser aprobado este no tendría la validación necesaria en España.** 	

## Sistema de actuación y sensorización

* Se utilizarán motores NEMA, concretamente NEMA 24 que si bien no son tan comunes como los NEMA 23 dan un par motor suficiente. En los prototipos hemos utilizado motores de 4 Newton metros. En cualquier caso el uso de otro tipo de motores debe garantizar la suficiente presión sobre el globo del Jackson-Rees para producir el suficiente flujo ventilatorio. (Se hicieron pruebas con nema 17 y no daban sufiente par motor, seguramente algunos nema 23 puedan ser suficiente).

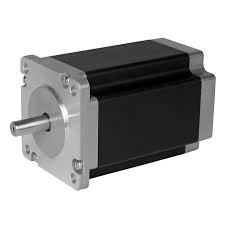
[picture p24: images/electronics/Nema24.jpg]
Nema 24 Motor Nema 24


* Los motores NEMA se controlarán con un driver para motores paso a paso que proporcione la intensidad suficiente para comandar el motor elegido. El modelo utilizado en el prototipo está en el siguiente esquemma, el ZDM-2HA865. Se ha elegido este modelo ya que puede controlar tanto el NEMA24 como motores más pequeños sin necesidad de cambiar todo el hardware.

Esquema de conexión Esquema de conexión del driver y el motor paso a paso

* Para monitorizar la posición inicial del sistema, se utilizará un sensor de efecto hall o un simple final de carrera, (aunque también se ha considerado la opción de un segundo sensor para evitar problemas).

* Electroválvula de 24V para el control de salida de aire del sistema neumático, (en el prototipo original se utilizaron 2 porque eran de un diámetro demasiado pequeño como para permitir un caudal apropiado).

* Sensor de caudal Sensirion SFM3300-AW para la medición del caudal en el espacio muerto del sistema de ventilación. Al ser una pieza que estará en contacto con el circuito de inspiración del paciente, se emplea un sensor homologado para aplicaciones médicas. (Si este modelo no estuviera disponible se pueden buscar sustitutos y con pequeñas modificaciones del código se podrían utilizar igualmente).

Caudalímetro

* Sensor de presión diferencial para la diferencia de presión que existe entre el circuito inspiratorio y la presión ambiental. Se ha empleado el modelo ABPLANT001PG2A5 de Honeywell, que está homologado para aplicaciones médicas. (En versiones previas utilizamos 2 BME280 conectados por SPI). 

En la tabla siguiente podemos ver el pinout utilizado en el prototipo:

| USO                   |PIN |
| --------------------- | -- |
| PIN_STEPPER_STEP      |  6 |
| PIN_STEPPER_DIRECTION |  7 | 
| PIN_STEPPER_EN STEP   |  8 |
| PIN_STEPPER_ALARM     |  3 | 
| PIN_BUZZ              | 11 |
| PIN_STEPPER_ENDSTOP   |  2 | 
| PIN_SOLENOID          | 39 |
| PIN_RELAY             | 25 | 

A continuación se puede muestra el pinout del Arduino con todos los componentes, sensores, alarma, actuadores, protocolos de comunicación...etc.
PinOut MCU Pin Out de la electrónica con el Arduino

El diagrama de bloques de la placa de circuito impreso diseñada para la versión del arduino, está disponible en el siguiente enlace:

**[Diagrama de Bloques](https://gitlab.com/reespirator/reespirator2020/-/blob/master/electronics/arduino/diagrama_bloques_esquema.md "Diagrama de Bloques")**

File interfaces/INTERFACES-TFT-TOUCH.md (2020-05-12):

## Interface TFT-Touch

Para pantalla visualizar las gráficas de funcionamiento del Reespirator 2020 y poder interactuar con el dispositivo podemos utilizar una pantalla TFT táctil conectada a una Raspberry Pi o una Beagle Bone. En el prototipo original Reespirator 23 se utilizó una BeagleBone con una pantalla TFT táctil de 7" que es lo se tenía disponible en ese momento, sin embargo dado que se empleó Python, el código es fácilmente adaptable a otras plataformas como Raspberry Pi o similares.
Mediante comunicación serie, el Arduino Mega del sistema de control envía y recibe los datos necesarios para monitorizar y manejar el dispositivo.

Actualmente (19/04/2020), la única combinación que está completamente funcional corresponde al uso de la BeagleBone con el último firmware de Arduino para Reespirator 23, ambos están disponibles en los repositorios de los siguientes enlaces: https://gitlab.com/reesistencia

Para utilizar una Raspberry Pi no debería ser muy diferente que con BeagleBone, es necesario configurar el Python que en las distribuciones de Raspbian suelen estar incluidas e instalar algunas librerías como PyQt pero el software de visualización/interacción debería funcionar igualmente. En el siguiente enlace se describe por ejemplo como instalar Qt5: https://wiki.qt.io/Raspberry_Pi_Beginners_Guide/es 

> John Gamarra comenta, que para que funcione en una RPi, no funciona con la instalacion manual, ha tenido que actualizar una libreria PyQt5 a 5.14.2 pero despues de un tiempo, la instalacion se cuelga en preparing wheel metadata, por lo que debo correr la interfaz por comando...

Desde el siguiente enlace se puede descargar el [Manual de usuario del interfaz táctil usado en el prototipo original](https://gitlab.com/reespirator/reespirator2020/-/raw/master/files/pdf/Manual-Usuario-Reespirator-UI.pdf "Manual de usuario del interfaz táctil").

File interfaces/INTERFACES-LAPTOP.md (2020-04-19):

## Interface por ordenador (PC, portátil...)

Mediante el uso de comunicaciones serie el dispositivo basado en Arduino se puede manejar desde un PC o un portátil enviando las instrucciones desde el PC y visualizando las gráficas del dispositivo en la pantalla del ordenador.

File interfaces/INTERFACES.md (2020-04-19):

## Interfaces

Los distintos modelos de Reespirator 2020 utilizan diferentes tipos de interfaces de usuario según la disponibilidad en el lugar de fabricación.

El modelo con PLC utiliza una pantalla táctil [HMI](https://gitlab.com/reespirator/reespirator2020/-/blob/master/interfaces/INTERFACES-HMI.md) lo que permite gran versatilidad y facilidad de uso; pero en los sitios dónde esto no es posible se puede utilizar para el modelo de Arduino una simple [pantalla LCD y un encoder](https://gitlab.com/reespirator/reespirator2020/-/blob/master/interfaces/INTERFACES-LCD-ENCODER.md) u otras configuraciones diferentes como por ejemplo un [PC conectado por puerto serie](https://gitlab.com/reespirator/reespirator2020/-/blob/master/interfaces/INTERFACES-LAPTOP.md) al Arduino o una [pantalla táctil](https://gitlab.com/reespirator/reespirator2020/-/blob/master/interfaces/INTERFACES-TFT-TOUCH.md) conectada a una Raspberry Pi o una Beagle Bone. En todos estos casos un software programado en *Python* permite representar los datos enviados desde el bloque de control en la pantalla correspondiente y enviar desde el dispositivo apropiado las órdenes de cambio de parámetros al bloque de control.

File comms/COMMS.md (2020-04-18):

## Comunicaciones

El respirador Reespirator 2020 en su versión Arduino utiliza comunicaciones serie para recibir las instrucciones del médico desde un interfaz externo basado en una pantalla táctil sobre Raspberry Pi o Beagle Bone, por ejemplo. También puede comunicarse con un ordenador mediante el puerto USB y en caso de necesidad podría manejarse con un ratón desde un PC o portátil mediante un software Python que permite visualizar y cambiar los parámetros del respirador.

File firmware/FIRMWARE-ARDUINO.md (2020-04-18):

## Firmware Arduino

El firmware para el Arduino Mega está en el repositorio [reespirator-firmware](https://gitlab.com/reesistencia/reespirator)

Otro grupo de programadores está reorganizando y refactorizando el código para hacerlo más sólido:
[https://gitlab.com/reespirator-arduino/reespirator](https://gitlab.com/reespirator-arduino/reespirator)

Hay que tener en cuenta que para la versión con Arduino se han barajado al menos 3 configuraciones distintas:

* 1 LCD de 20 caracteres x 4 líneas y un encoder.
* 1 LCD de 20 caracteres x 4 líneas y cuatro encoders o 1 encoder y 4 botones.
* 1 Pantalla gráfica táctil con otro dispositivo externo como una beagle-bone, una Raspberry Pi o un portátil o PC de escritorio conectados por puerto serie.

El software para la Beagle-bone y la pantalla utilizadas en el prototipo Reespirator 23 fue programado en Python y está disponible en el repositorio [reespirator-beagle-touch](https://gitlab.com/reesistencia/reespirator-beagle-touch) 

En otros grupos de Telegram se ha logrado hacer funcionar este mismo código de visualización en un portátil y en una Raspberry Pi.

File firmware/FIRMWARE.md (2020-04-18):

## Firmware
El sistema de control necesita ser programado con un firmware que permita hacer funcionar el dispositivo. Dicho programa se ha realizado conforme a las especificaciones de los especialistas médicos para realizar las funciones para las que el dispositivo fue diseñado.

El firmware para el Arduino Mega está en el repositorio [reespirator-firmware](https://gitlab.com/reesistencia/reespirator)

Otro grupo de programadores está reorganizando y refactorizando el código para hacerlo más sólido:
[https://gitlab.com/reespirator-arduino/reespirator](https://gitlab.com/reespirator-arduino/reespirator)

Hay que tener en cuenta que para la versión con Arduino se han barajado al menos 3 configuraciones distintas:

* 1 LCD de 20 caracteres x4 líneas y un encoder.
* 1 LCD de 20 caracteres x 4 líneas y cuatro encoders.
* 1 Pantalla gráfica táctil con otro dispositivo externo como una beagle-bone, una Raspberry Pi o un portátil o PC de escritorio conectados por puerto serie.

El software para la Beagle-bone y la pantalla utilizadas en el prototipo Reespirator 23 fue programado en Python y está disponible en el repositorio [reespirator-beagle-touch](https://gitlab.com/reesistencia/reespirator-beagle-touch) 

En otros grupos de Telegram se ha logrado hacer funcionar este mismo código de visualización en un portátil y en una Raspberry Pi.

En cuanto al software para la configuración con un PLC se ha preparado sobre un PLC Siemens 1200 y un HMI si bien se está considerando también la posibilidad de portarlo a otros sistemas.

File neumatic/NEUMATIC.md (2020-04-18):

## Sistema neumático
Basado en un sistema [Jackson-Rees](https://en.wikipedia.org/wiki/Breathing_circuit), **Reespirator** es un respirador que además del mencionado sistema médico Jackson-Rees utiliza una serie de elementos neumáticos utilizados para entubar al paciente y para controlar sus flujos de respiración inspiratorios y espiratorios.

Sistema Jakson-Rees Sistema Jackson-Rees

Esquema neumático

El circuito neumático completo está compuesto por tres secciones:
* Circuito de inspiración, resaltado en rojo en el diagrama
* Circuito de paciente, resaltado en verde en el diagrama
* Circuito de espiración, resaltado en azul en el diagrama

El circuito de inspiración (rojo) está compuesto por los siguientes elementos:
Línea de entrada de aire+O2 (1) proporciona el gas que respira el paciente. Deberá proporcionar un caudal en exceso sobre el caudal medio programando. La mezcla se realizará de forma externa al sistema, dependiendo de las capacidades de cada hospital:
En caso de que sólo exista una botella de oxígeno, se podría hacer una mezcla usando una válvula de venturi
En caso de que existan líneas separadas de oxígeno y aire, se podrá hacer una mezcla con válvulas y rotámetros para controlar la proporción de mezcla.
Balón del Mapleson o Jackson Rees (2) es accionado por el mecanismo motorizado y leva durante el ciclo de inspiración. Durante el ciclo de espiración la leva vuelve a posición de reposo para permitir que la línea de entrada (1) rellene el balón.

El circuito de inspiración (rojo) se comunica con el circuito de paciente (verde) por medio de la válvula anti-retorno (3).

El circuito de paciente (verde) está compuesto por los siguientes elementos:
Válvula de alivio de presión (4) o de seguridad: protege al paciente de sobrepresiones que pudieran suceder en el circuito, por un comportamiento incorrecto del respirador o por espasmos u otros movimientos causados por el propio paciente durante el ciclo de inspiración. La normativa indica que esta válvula de seguridad debe ser menor de 80 cmH2O, y lógicamente ha de ser mayor que la presión inspiratoria máxima que se desee que tenga el sistema, que típicamente rondará los 40 cmH2O.
Bloque de sensor (5): proporciona una medida de caudal y de presión en el circuito de paciente. Su cableado de medida se conecta a la caja del respirador mediante un conector Estará conectado a la caja del respirador a un terminal de conexión de los sensores (6). La medida de caudal se realiza mediante el método de placa orificio. Se mide la pérdida caída de presión del flujo del aire al atravesar un orificio de características conocidas. Se utiliza un sensor de presión diferencial que mide la diferencia de presiones, y también un sensor manométrico (o gauge) que proporciona una medida de la presión. El uso de estos sensores de presión para medir el caudal tiene como principales ventajas su reducido coste y alta disponibilidad en comparación con sensores de tipo caudalímetro. Inicialmente se contemplan dos opciones, en cuanto a la forma en que se realiza la medida de caudal:
Por placa orificio. Se mide la pérdida caída de presión del flujo del aire al atravesar un orificio de características conocidas. La conexión de este punto a la caja del respirador se puede realizar por medio de dos tubos, estando los sensores en el interior del respirador. Se necesita un sensor de presión diferencial que mida la dicha diferencia de presiones, y también un sensor manométrico (o gauge) que proporciona una medida de la presión. Como ventaja, se simplifica el número de elementos externos a la caja del respirador (dos tubos), y su coste y disponibilidad, dado que los sensores de presión son abundantes y baratos.
Caudalímetro tipo mass-flow. Produce una medida directa del caudal. Requiere la conexión de cables de alimentación y comunicación desde la caja del respirador hasta el sensor. Adicionalmente es necesario obtener una medida de presión que típicamente el sensor de caudal no proporciona. Esta medida se obtendría mediante un sensor manométrico o gauge, que podría estar situado junto al medidor de caudal (aprovechando que de todas maneras hay que llevar conexiones eléctricas hasta este punto) o podría estar en la caja del respirador, comunicado con el circuito de paciente mediante un tubo. 
Filtro (7): su función es purificar el aire tanto a la entrada como a la salida del paciente.  

El circuito de paciente (verde) se comunica con el circuito de espiración (azul) por medio de la válvula anti-retorno (8).

El circuito de espiración (azul) está compuesto por los siguientes elementos:
Electroválvula (9)
Válvula PEEP regulable (10): su objetivo es el mantenimiento de una presión mínima en el sistema durante la espiración para evitar el colapso pulmonar. Esta válvula se regula automáticamente para conseguir la presión PEEP establecida por el médico en el display del respirador. es de regulación automática mediante un sistema de electroválvulas, lo que permite al médico instaurarlo en el propio display.

Biocompatibilidad
Todos los elementos del circuito de inspiración (rojo) y circuito de paciente (verde), incluidas las válvulas anti-retorno (3) y (8) deben ser medical-grade, ya que el aire que circula por ellos es insuflado en los pulmones del paciente

El aire que circula los elementos del circuito de espiración (azul) nunca retorna a los pulmones del paciente gracias a la válvula anti-retorno (8), por lo cual no es necesario que sean medical-grade.

Reusabilidad
Los elementos del circuito de inspiración (rojo) se ven protegidos del aire espirado por el paciente por la válvula anti-retorno (3), por lo cual no se contaminarán y se pueden reutilizar.

Los elementos del circuito de espiración (azul) sí son contaminados, pero el aire en contacto con ellos nunca debería entrar en contacto con un nuevo paciente, gracias a la válvula anti-retorno (8), con lo cual son, también, reutilizables.

Los elementos del circuito de paciente (verde) son contaminados y su uso en un nuevo paciente sin previa esterilización no debería permitirse (salvo que la confianza en el filtro (7) sea plena). El bloque sensor y sus sensores también se contaminan y deberán ser sustituidos para cada nuevo paciente. Si se opta por una opción de sensores en la que dichos sensores están dentro de la caja del respirador, pero conectados por tubo(s) al circuito de paciente,  estos sensores, siendo estrictos, también deberían ser reemplazado o esterilizados.

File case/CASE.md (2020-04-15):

## Estructura básica
Reespirator 2020 puede fabricarse como ya hemos comentado en 2 versiones diferentes. 
La caja puede fabricarse también de dos formas distintas mediante corte láser o fresado de metacrilato o madera y mediante plegado de chapa-

* La versión de [metacrilato / madera / mdf](https://gitlab.com/reespirator/reespirator2020/-/blob/master/case/CASE-METHACRYLATE.md) es de tipo machiembrado como la que aparece en la figura para facilitar su montaje.



* La versión de [chapa plegada](https://gitlab.com/reespirator/reespirator2020/-/blob/master/case/CASE-LOCK.md) tiene el siguiente aspecto:
Diagrama de bloques Caja para fabricar en chapa plegada

Los archivos para su fabricación en distintos formatos se están publicando en el directorio /files.

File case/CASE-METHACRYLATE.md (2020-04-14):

## Estructura básica en metacrilato o MDF
Reespirator 2020 puede fabricarse como ya hemos comentado en 2 versiones diferentes. 
La caja puede fabricarse también de dos formas distintas mediante corte láser o fresado de metacrilato o madera y mediante plegado de chapa-

* La versión de metacrilato / madera / mdf es de tipo machiembrado como la que aparece en las siguiente figuras para facilitar su montaje. 

Caja completa

> La siguiente información es de una primera versión de Reespirator 2020 se está actulizando toda la documentación a medida que la vamos teniendo disponible. Debe tenerse en cuenta que al fabricar puede que haya ajustar una décima de milímetro las medidas para el corte.

Reespirator 2020 consta de una caja diseñada para fabricarse mediante corte láser modificados a partir de los diseños originales de Reesistencia Team y que contiene casi todos elementos del respirador en su interior. 

Los archivos para su fabricación mediante corte láser o fresado (CNC) se encuentra en el directorio [/files/cut](https://gitlab.com/reespirator/reespirator2020/-/tree/master/files/cut "files/cut"), estamos trabajando para ofrecerlos en archivos separados y en varios formatos.

En los archivos compartidos se encuentran varias versiones de tapa para el hueco de la pantalla en función del tipo de display utilizado.

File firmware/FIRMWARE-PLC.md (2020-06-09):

## Firmware del PLC

En cuanto al software para la configuración con un PLC se ha preparado sobre un PLC Siemens 1215 y un HMI si bien se está considerando también la posibilidad de portarlo a otros sistemas.

La configuración del TIA Portal para configurar el autómata y el HMI para su programación:

En esta imagen podemos apreciar el modelo exacto del PLC SIEMENS S7 1200 1215c utilizado:

Detalle del PLC

La siguiente imagen muestra la configuración básica del HMI modelo TP700 utilizado en nuestro prototipo:

Detalle del HMI Detalle del PLC

En esta imagen mostramos la configuración de red utilizada para conectar el PLC y el HMI:

Detalle de la conexión Detalle de las conexiones entre el autómata y el HMI

Las siguientes son alguana de las imágenes del software ejecutándose en el HMI:

HMI 1

HMI 2

HMI 3

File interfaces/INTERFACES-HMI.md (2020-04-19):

## Interface HMI

El modelo de Reespirator 2020 con PLC utiliza una pantalla táctil HMI lo que permite gran versatilidad y facilidad de uso.

SIMATIC HMI Touch Interface SIMACTIC HMI Touch

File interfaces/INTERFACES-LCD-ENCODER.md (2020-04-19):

## Interface LCD + Encoder + 4 pulsadores

Los distintos modelos de Reespirator 2020 utilizan diferentes tipos de interfaces de usuario según la disponibilidad en el lugar de fabricación.

El primer prototipo incluía simplemente un Arduino y una simple pantalla LCD y un encoder y con esta configuración se lograron hacer las primeras pruebas preclínicas, también se consideró la posibilidad de usar botones en lugar de encoders porque podían resultar más rápidos para cambiar las configuraciones en ciertos momentos críticos del tratamiento; pero finalmente se optó por una configuración basada en 
- una pantalla LCD de 20x4
- un encoder
- 4 pulsadores
- un zumbador

Los médicos consideraron que si bien podría ser suficiente, era más conveniente incluir una pantalla gráfica para representar las señales producidas por el respirador. 

Configuración LCD+Encoder+Pulsadores

>La versión con pantalla LCD, encoder y pulsadores se documenta aquí para aquellos lugares donde no se puedan implementar las soluciones gráficas, y además utilizando un ordenador es posible visualizar las gráficas y se puede utilizar igualmente esta configuración básica.

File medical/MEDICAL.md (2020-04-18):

## ¿Qué eson los respiradores y para qué sirven?

En el siguiente enlace la Biblioteca Nacional de Medicina de EE.UU. nos da una descripción sencilla de [¿qué son los respiradores?](https://medlineplus.gov/spanish/ency/patientinstructions/000458.htm "¿Qué son los respiradores")

## Información médica básica del dispositivo Reespirator 2020

El dispositivo Reespirator 2020 es un dispositvo para uso médido diseñando para intentar cumplir las siguientes [especificaciones clínicas](https://foro.coronavirusmakers.org/index.php?p=/discussion/44/especificaciones-clinicas-de-un-respirador-util-en-esta-crisis#latest)

Los dispositivos que estamos prototipando podrán funcionar en los siguientes modos. *Los dos primeros están completos y se está trabajando para finalizar los otros dos.*

**Modo controlado**
La máquina suple totalmente la ventilación del paciente pudiendo controlar tanto el volumen como la presión, sensando la medida contrapuesta.

En caso de encontrarnos en la modalidad de control por presión, los parámetros a controlar son la presión inspiratoria máxima, o PIP, (10 - 60 cmH2O), la frecuencia respiratoria (3 - 35 respiraciones por minuto) y la presión positiva al final de la espiración, o PEEP (3 - 30 cmH2O). En este modo se realiza un sensado del volumen minuto, extrapolando con ello el volumen tidal que se está administrando con cada inspiración.

Por otro lado, en su modalidad de control por volumen, se podrán controlar los mismos parámetros antes descritos salvo la presión inspiratoria, que en este caso solo sería sensada. El volumen tidal controlable con la máquina estará entre 150 y 900 ml, lo cual implica un peso mínimo del paciente de 40kg, considerando a pacientes con peso inferior como pediátricos, los cuales quedarían fuera de las especificaciones de este dispositivo.

Por defecto, la máquina se inicia en modo controlado por presión y consigna unos valores de 12 r/min, PIP de 18 cmH2O y PEEP de 6 cmH2O.

**Modo respiración asistido invasivo**
El modo de respiración asistida (o trigger) asiste a la respiración del paciente. Cuando se detecta una respiración espontánea (fijando un umbral de caudal o presión y detectando cuándo los valores exceden ese umbral) se dispara el ciclo respiratorio.

Este sistema obliga a la instauración de un número mínimo de ventilaciones de rescate, las cuales se marcarán como frecuencia respiratoria en caso de tener activado el trigger, mecanismo con el cual se permite un sistema de rescate al trigger. El número mínimo de ventilaciones de rescate es de 3.

La variable a monitorizar será el caudal inspiratorio y el umbral por defecto viene prefijado a 3 litros por minuto, pudiendo modificarse para facilitar el disparo del trigger por parte del paciente.

**Modo respiración asistido no invasivo**
Este modelo de ventilador puede utilizarse para ventilación mecánica no invasiva, incluyendo la posibilidad de modalidad BIPAP y modalidad CPAP. 

La modalidad de BIPAP representa un aprovechamiento del sistema de trigger implementado en el sistema de respiración asistida invasiva. Este modelo es viable al utilizar flujos altos con la máquina que permiten un lavado de CO2 eficaz así como compensación de fugas.

El ventilador permite igualar los parámetros de PIP y PEEP, lo que permite la utilización del sistema como máquina de CPAP aplicando únicamente una PEEP, en esta modalidad dada la construcción de la máquina se inactiva el sistema de trigger y elimina las ventilaciones de rescate.

**Modo de reclutamiento alveolar**
Se establece un modo de uso mediante un botón de emergencia, destinado a realizar una operación clínica de reclutamiento alveolar. Mediante dicha maniobra, el sistema aplicará una presión constante de inspiración de 40 cmH2O durante un tiempo máximo de 40 segundos. Una vez entrado en este modo, se activará la alarma acústica pertinente. Se podrá volver al modo de funcionamiento normal, antes de los 40 segundos, a través de la interfaz táctil de la máquina, según el criterio clínico del médico usuario.

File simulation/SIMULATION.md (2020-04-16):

## Simulación

Los modelos matemáticos que subyacen a los modos de control en lazo cerrado del Reespirator 2020 se representan en los siguientes esquemas:

Lazos cerrados de control

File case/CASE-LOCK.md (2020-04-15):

## Estructura básica en chapa plegada
Reespirator 2020 puede fabricarse como ya hemos comentado en 2 versiones diferentes. 

La caja puede fabricarse también de dos formas distintas mediante corte láser o fresado de metacrilato o madera y mediante plegado de chapa.

Los archivos para su fabricación mediante chapa plegada en distintos formatos se están publicando en el directorio [/files/chapa](https://gitlab.com/reespirator/reespirator2020/-/tree/master/files/chapa "files/chapa").

* La versión de chapa plegada de 1mm tiene el siguiente aspecto:

Caja completa

Otra vista de la caja completa

Carcasa superior Carcasa superior para fabricar

Carcasa superior Carcasa superior para fabricar

Anillo culo Carcasa superior para fabricar

Separador inferior Carcasa superior para fabricar

Separador superior

Laterales abatibles

Culo cubierta

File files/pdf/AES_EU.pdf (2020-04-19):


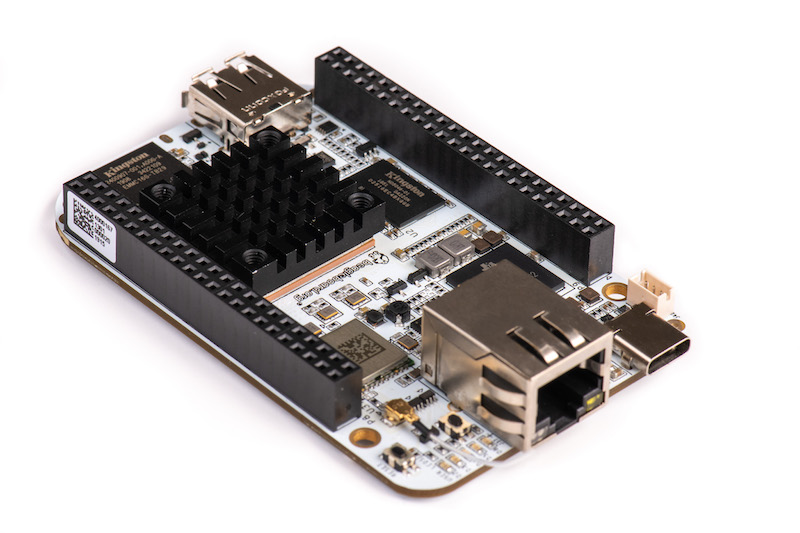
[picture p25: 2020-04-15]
images/electronics/BeagleBone.jpg

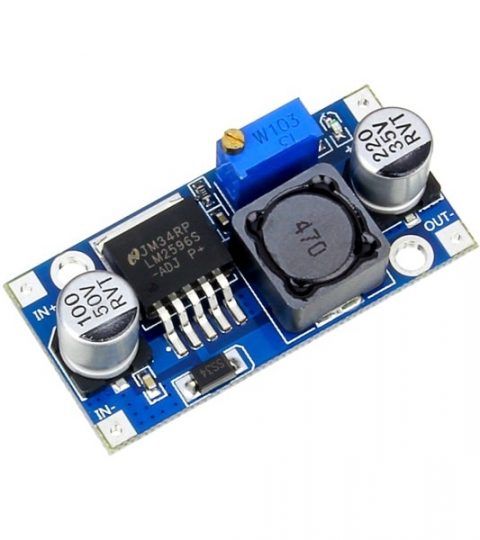
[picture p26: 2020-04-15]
images/electronics/Módulo-LM2596-convertidor-de-voltaje.jpg

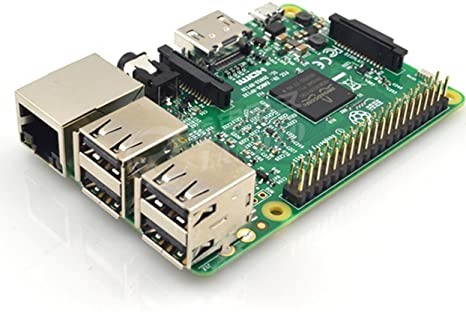
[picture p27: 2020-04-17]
images/electronics/Raspberry-Pi.jpg

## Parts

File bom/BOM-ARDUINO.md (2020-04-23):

# Lista de materiales

La lista de materiales para construir un Reespirator 2020 versión Arduino incluye los siguientes componentes:

* **Estructura**

Para construir el respirador tenemos que fabricar una caja para contener los componentes principales del mismo. Esta puede construirse tanto en metacrilato, como en madera, MDF o incluso utilizar el diseño de chapa plegada. 
Evidentemente escoger un material u otro o el tipo de caja dependerá de las posibilidades del lugar donde se vaya a fabricar.
Para el modelo low-cost basado en Arduino lo lógico es la caja fabricada por corte láser en metacrilato, madera o MDF según los materiales disponibles. 
** Esta caja no cumple normativas de seguridad o de compatibilidad electromagnética; pero será suficiente para un prototipo y en aquellos casos dónde sea la única opción.**
Los archivos para el corte láser están accesibles desde el siguiente enlace a la caja de metacrilato.

https://gitlab.com/reespirator/reespirator2020/-/tree/master/files/cut/corte

* **Sistema neumático**

Todo el Reespirator 2020 se basa en la utilización de un sistema Jackson-Rees.

* **Mecánica**

Para la parte mecánica es necesario cortar algunas piezas como las de la caja para construir la leva y el balancín que actuan sobre el balón del Jackson-Rees, así como imprimir algunas piezas en 3D como la cuna para el balón o la pala/empujador del mismo.

* **Electrónica**

Para montar la electrónica low-cost partiremos de la utilización de un Arduino Mega 2560 al que conectaremos actuadores y sensores. 
Estos pueden conectarse directamente con los cables al Arduino aunque se recomienda encarecidamente su soldadura o emplear una shield o protoboard que garantice buenas conexiones eléctricas.
Se ha diseñado una PCB para aquellos casos en los que esta pueda obtenerse, esta simplifica enormemente el montaje del dispositivo y mejora la fiabilidad de la electrónica. La pcb diseñada contará en su gran mayoría con componentes de montaje superficial SMD, 
por lo que se podrá encargar su montaje, directamente a la empresa que realice la fabricación de las placas de circuito impreso. En este sentido se ha realizado un gran trabajo de diseño, para asegurar la placa ante incompatibilidades electromagnéticas.

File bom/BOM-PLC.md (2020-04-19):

# Lista de materiales

La lista de materiales para construir un Reespirator 2020 modelo PLC incluye los siguientes componentes:

**Estructura**
- Caja de chapa plegada

**Sistema neumático**
- Sistema Jackson-Rees
- Tubuladura

**Mecánica**
- Leva
- Balancín
- Rodamiento 608Z
- Acople para el motor
- Tornillería
- Cuna para el balón impresa en 3D
- Pala/Empujador impreso en 3D

**Electrónica**
- Toma de alimentación IEC
- Fuente de alimentación 24V
- Autómata PLC Siemens S7-1200
- HMI SIMATIC 7"
- Motor Nema 24
- Driver ZDM-2HA865
- Sensor inductivo cilíndrico AES/AP-3A
- Caudalímetro
- Sensor de presión diferencial

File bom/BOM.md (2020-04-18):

# Lista de materiales

La lista de materiales para construir un Reespirator 2020 es cuando menos complicada, incluye elementos como metacrilato, madera, MDF o chapa para la caja, sistmeas electrónicos como un Arduino Mega o un autómata PLC, y otros componentes, pero también elementos mecánicos y otros incluso impresos en 3D; pero sobre todo requiere también de la utilización de sistemas médicos tales como tubuladuras y un sistema ventilatorio Jackson-Rees.

Según el modelo que se quiera construir la lista de materiales cambia.

* [Lista de materiales para modelos low-cost](https://gitlab.com/reespirator/reespirator2020/-/blob/master/bom/BOM-ARDUINO.md "Lista de materiales para modelos low-cost") 
* [Lista de materiales para modelos pro](https://gitlab.com/reespirator/reespirator2020/-/blob/master/bom/BOM-PLC.md "Lista de materiales para modelos pro]")

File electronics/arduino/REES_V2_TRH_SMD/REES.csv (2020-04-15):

Id | Designator | Package | Quantity | Designation | Supplier and ref
1 | CK1 | L_CommonMode_Wuerth_WE-SL2 | 1 | CYSCM0905RTL-501
2 | J9 | RJ45_Hanrun_HR911105A | 1 | RJ45_Shielded
3 | J3 | TerminalBlock_Phoenix_MKDS-3-5-5.08_1x05_P5.08mm_Horizontal | 1 | Pulsadores
4 | H1,H4,H3,H2 | HOLES_3,6 | 4 | HOLES_MOUNT-HOLE3.6
5 | Arduino1 | Arduino_Mega2560_Shield | 1 | Arduino_Mega2560_Shield
6 | SW1 | PEC12_INCREMENTAL_ENCODER | 1 | Encoder1
7 | LCD1 | L2034-T | 1 | LCD_L2034_T
8 | BZ1 | Buzzer_CUI_CPT-9019S-SMT | 1 | MLT-9650
9 | C1,C2,C38,C39,C40,C41 | C_0603_1608Metric | 6 | 27nF
10 | C7,C25,C26 | CP_Elec_10x10.5 | 3 | 330uF
11 | C9 | C_0603_1608Metric | 1 | 10nF
12 | C11,C32,C33,C18,C36,C37 | C_0603_1608Metric | 6 | 100nF
13 | C12,C13,C14,C15 | C_0603_1608Metric | 4 | 1.5nF
14 | C16,C20 | CP_Elec_10x10.5 | 2 | 1000uF
15 | C23,C24,C30,C17,C19 | C_0603_1608Metric | 5 | 1uF
16 | C31,C35 | C_0603_1608Metric | 2 | 100pF
17 | D1 | D_SMA | 1 | 1N4007
18 | D3,D4,D5,D6 | D_SOD-123 | 4 | 1N4148
19 | D7 | D_SMA | 1 | B340AF-13
20 | D8,D9,D10,D2,D11,D12,D13,D14 | D_SOT-23_ANK | 8 | BAS40
21 | R5 | R_0805_2012Metric | 1 | 100R
22 | R6,R19,R88,R91 | R_2512_6332Metric | 4 | 1K2 1W
23 | R7,R20,R43,R44,R45,R46,R47,R48,R89,R92 | R_1206_3216Metric | 10 | 2K2
24 | R9 | R_0603_1608Metric | 1 | 3K24
25 | R10,R77 | R_0603_1608Metric | 2 | 10K
26 | R16,R17,R3,R4,R8,R21,R28,R29,R31,R32,R36,R37,R85,R86,R90,R93,R42,R50,R51,R69,R71,R79,R81 | R_1206_3216Metric | 23 | 1K
27 | R24,R25,R26,R27 | R_0805_2012Metric | 4 | 10K
28 | R34,R35 | R_0603_1608Metric | 2 | 3K3
29 | R39 | R_0805_2012Metric | 1 | 3K3
30 | R52,R55,R11,R12 | R_0603_1608Metric | 4 | 200K
31 | R56,R57,R60,R63,R22,R23 | R_0603_1608Metric | 6 | 7K5
32 | R61,R62,R64,R65,R74,R75,R76,R40,R41 | R_1206_3216Metric | 9 | 120R
33 | R72,R73 | R_0805_2012Metric | 2 | 330R
34 | U3 | DIP-16_W7.62mm | 1 | L293
35 | U5,U8 | TSSOP-8_3x3mm_P0.65mm | 2 | PCA9306
36 | U6,U7,U11,U12,U13 | SOT-23-5_HandSoldering | 5 | SN74LV1T34
37 | K1 | Relay_SPDT_Omron-G5LE-1 | 1 | SRD-24VDC-SL-C
38 | R15 | R_1206_3216Metric | 1 | 10R
39 | RV1 | Potentiometer_Bourns_3214W_Vertical | 1 | 15K
40 | C34 | C_0603_1608Metric | 1 | 47nF
41 | F1 | Fuse_1812_4532Metric | 1 | mSMD075-33V
42 | U2 | TI_SO-PowerPAD-8_ThermalVias | 1 | TPS5430QDDARQ1
43 | CR1,CR2,CR3,CR5,CR6,CR10,CR16,CR47,CR48,CR49,CR50,CR51,CR55,CR56,CR58,CR59,CR61,CR67,CR68,CR69,CR70 | D_SOD-123F | 21 | SMF5.0A
44 | CR4,CR7,CR8,CR9,CR11,CR12,CR13,CR14,CR15,CR17,CR18,CR22,CR25,CR35,CR37,CR41,CR44,CR45,CR46,CR52,CR63,CR64,CR65,CR66,CR72 | D_SOD-123F | 25 | SMF3.3A
45 | CR19,CR20,CR21,CR23,CR24,CR26,CR27,CR28,CR29,CR30,CR31,CR32,CR33,CR34,CR36,CR38,CR39,CR40,CR42,CR43,CR53,CR54,CR57,CR60,CR62,CR71 | D_SOD-123F | 26 | SMF30A
46 | L1 | L_Bourns_SRR1210A | 1 | SWRB1204S-150MT
47 | L2,FB1,FB2,FB3,FB4,FB5,FB6,FB7,FB8,FB9,FB10,FB11,FB12,FB13,FB14,FB15,FB16,FB17,FB18,FB19,FB20,FB21,FB22,FB23,FB24,FB25,FB26,FB27,FB28,FB29,FB30,FB31,FB32,FB33,FB34,FB35,FB36,FB37,FB38,FB39,FB40 | C_1206_3216Metric | 41 | MLB3216-301P3A(f)
48 | NT1 | NetTie-4_SMD_Pad0.5mm | 1 | Net-Tie_4
49 | R49,R66,R67 | R_1206_3216Metric | 3 | 1K8
50 | U4,U9 | SOIC-18W_7.5x11.6mm_P1.27mm | 2 | ULN2803A
51 | U10 | Bosch_LGA-8_2x2.5mm_P0.65mm_ClockwisePinNumbering | 1 | SPL06-007
52 | R1,R2,R13,R14,R18,R30,R33,R38,R53,R54,R58,R59,R68,R70,R78,R80,R87 | R_0805_2012Metric | 17 | 560R
53 | U1,U14,U15 | SOIC-8_3.9x4.9mm_P1.27mm | 3 | MCP6002-xSN
54 | C3,C4,C5,C6,C8,C10,C21,C22,C27,C28,C29,C42 | C_1206_3216Metric | 12 | 10uF
55 | J11 | PinHeader_2x05_P2.54mm_Vertical_SMD | 1 | C124391
56 | J1,J7 | TerminalBlock_Phoenix_MKDS-3-4-5.08_1x04_P5.08mm_Horizontal | 2 | I2C3V3
57 | J2 | TerminalBlock_Phoenix_MKDS-3-2-5.08_1x02_P5.08mm_Horizontal | 1 | 24DC_IN
58 | J4 | TerminalBlock_Phoenix_MKDS-3-2-5.08_1x02_P5.08mm_Horizontal | 1 | Valvula0
59 | J5 | TerminalBlock_Phoenix_MKDS-3-2-5.08_1x02_P5.08mm_Horizontal | 1 | Valvula1
60 | J6 | TerminalBlock_Phoenix_MKDS-3-2-5.08_1x02_P5.08mm_Horizontal | 1 | Driver PWR
61 | J8 | TerminalBlock_Phoenix_MKDS-3-5-5.08_1x05_P5.08mm_Horizontal | 1 | SERIAL2
62 | J10 | TerminalBlock_Phoenix_MKDS-3-3-5.08_1x03_P5.08mm_Horizontal | 1 | LED0
63 | J12 | TerminalBlock_Phoenix_MKDS-3-2-5.08_1x02_P5.08mm_Horizontal | 1 | SAI_ALARM
64 | J14 | TerminalBlock_Phoenix_MKDS-3-3-5.08_1x03_P5.08mm_Horizontal | 1 | +5V
65 | J15 | TerminalBlock_Phoenix_MKDS-3-3-5.08_1x03_P5.08mm_Horizontal | 1 | GND
66 | J16 | TerminalBlock_Phoenix_MKDS-3-6-5.08_1x06_P5.08mm_Horizontal | 1 | DRIVER0
67 | J17 | TerminalBlock_Phoenix_MKDS-3-6-5.08_1x06_P5.08mm_Horizontal | 1 | DRIVER1
68 | J18 | TerminalBlock_Phoenix_MKDS-3-2-5.08_1x02_P5.08mm_Horizontal | 1 | FAN
69 | J19 | TerminalBlock_Phoenix_MKDS-3-7-5.08_1x07_P5.08mm_Horizontal | 1 | SPI0
70 | J20 | TerminalBlock_Phoenix_MKDS-3-4-5.08_1x04_P5.08mm_Horizontal | 1 | I2C0
71 | J22 | TerminalBlock_Phoenix_MKDS-3-8-5.08_1x08_P5.08mm_Horizontal | 1 | AnalogSens
72 | J25 | TerminalBlock_Phoenix_MKDS-3-4-5.08_1x04_P5.08mm_Horizontal | 1 | HALL
73 | J13 | TerminalBlock_Phoenix_MKDS-3-3-5.08_1x03_P5.08mm_Horizontal | 1 | +3V3

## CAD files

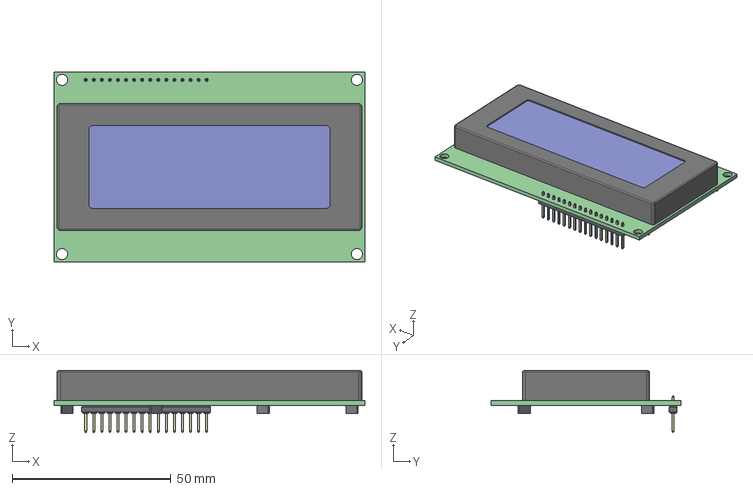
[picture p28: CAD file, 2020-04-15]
electronics/arduino/REES_V2_TRH_SMD/Modelos 3D/QP5522 Jaycar 20x4 LCD Module v14.step
98.0 x 60.0 x 19.5 mm

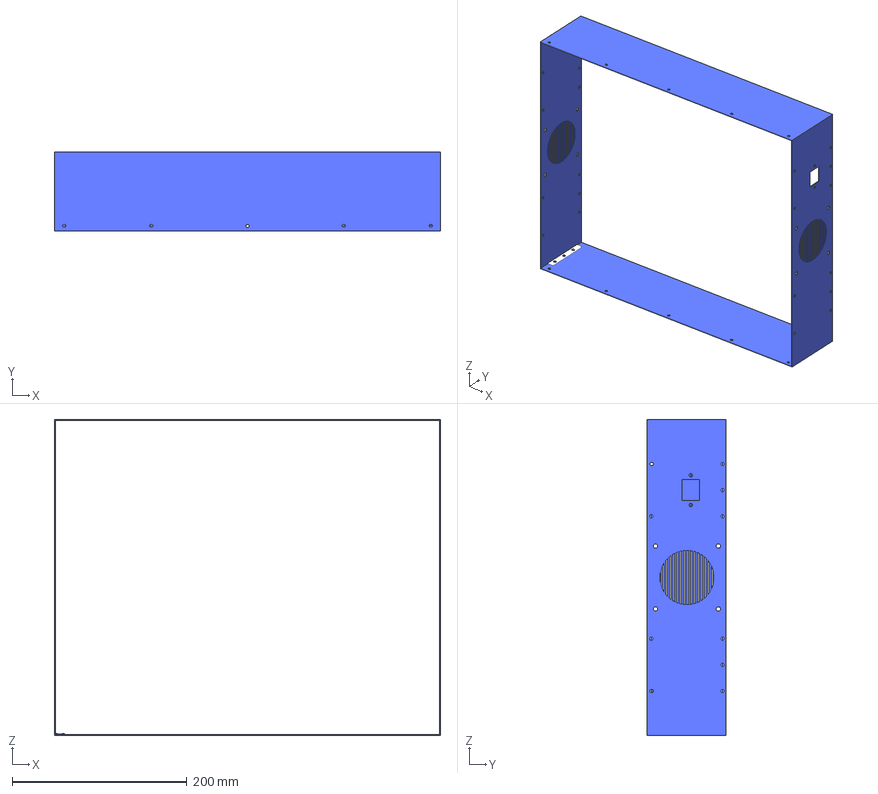
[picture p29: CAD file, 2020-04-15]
files/cut/chapa/bmr_003_anillo_culo_para_fabricar_con_rejilla.igs
442.0 x 91.0 x 362.0 mm

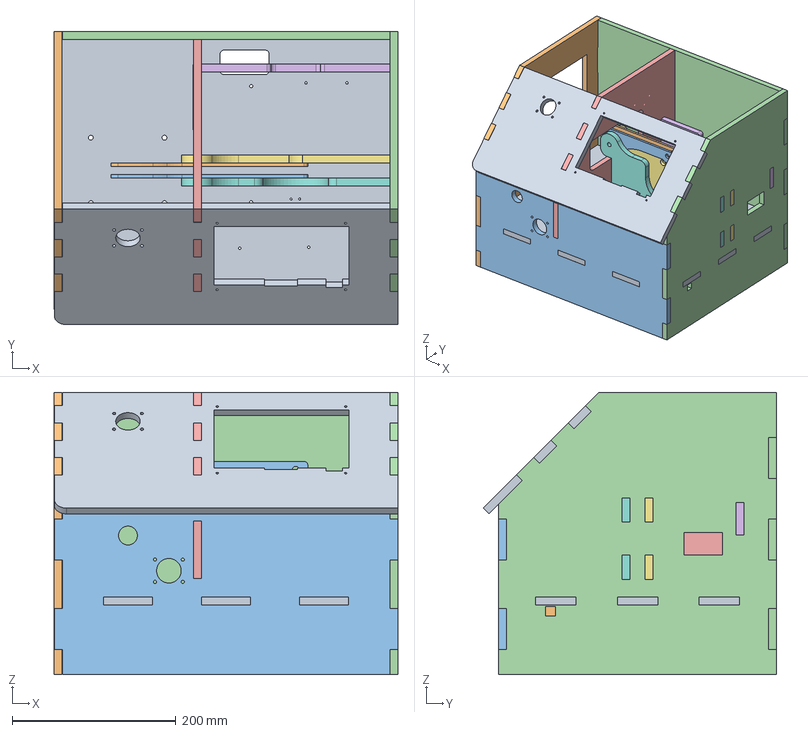
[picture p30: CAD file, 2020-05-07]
files/cut/corte/Version_2/Freecad/Montaje_Caja_v2.FCStd
420.4 x 358.6 x 345.0 mm
Base_metacrilato_001
Lateral_izquierdo_001
Frontal_001
Lateral_derecho_001
Separador_001
Soporte_Motor_001
Soporte_Leva_1_001
Soporte_Leva_2_001
Panel_Beaglebone_001
Balancin_v2_001
Balancin_v2_002
Trasera_001

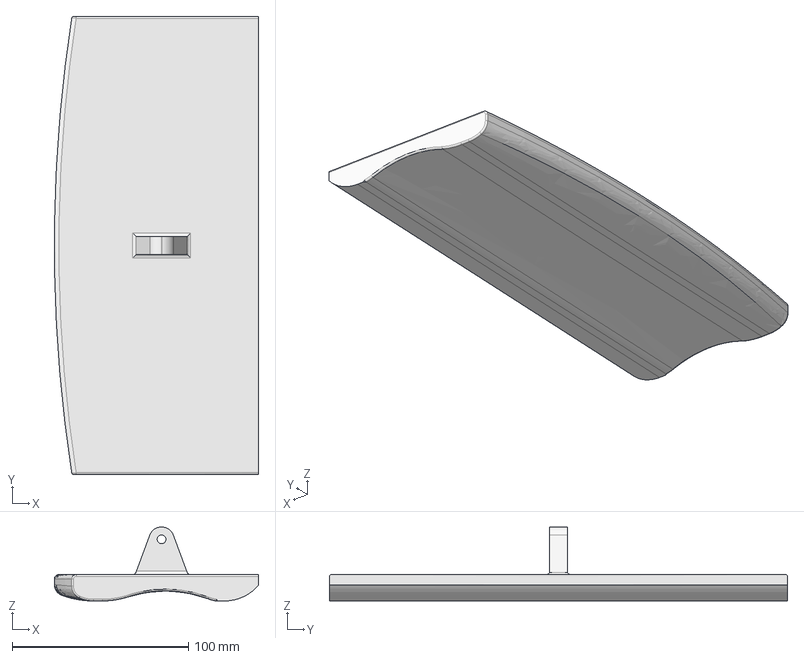
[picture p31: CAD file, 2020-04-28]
files/cut/corte/Version_2/STP/Pala_v3.step
116.0 x 260.0 x 42.0 mm

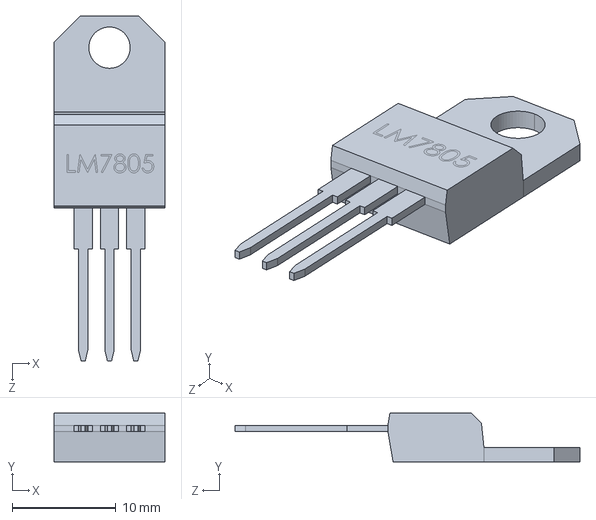
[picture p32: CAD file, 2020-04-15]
electronics/arduino/REES_V2_TRH_SMD/Modelos 3D/LM7805.STEP
10.7 x 4.70 x 33.2 mm

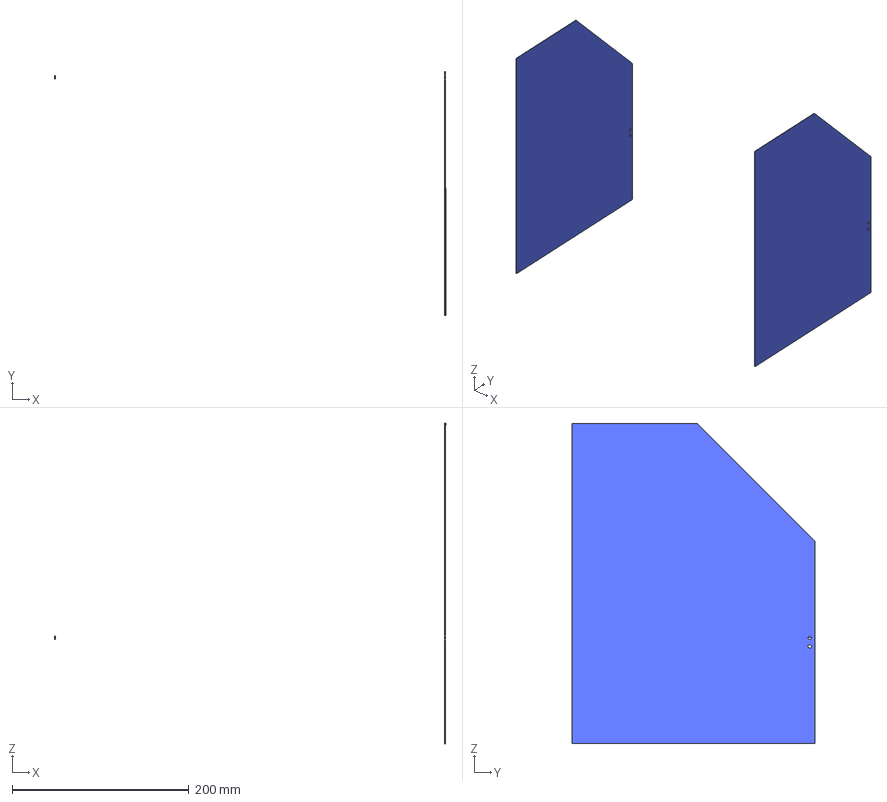
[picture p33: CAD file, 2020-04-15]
files/cut/chapa/bmr_006_laterales_abatibles_para_fabricar.igs
442.0 x 275.0 x 362.0 mm

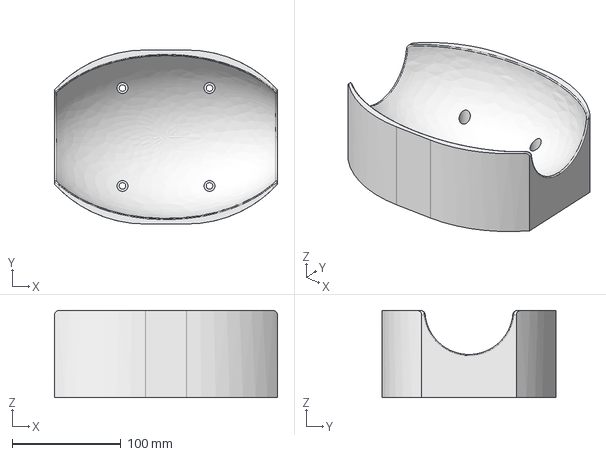
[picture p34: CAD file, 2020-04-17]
files/cut/corte/Version_2/STP/Cuna_V2.step
205.0 x 160.0 x 80.0 mm

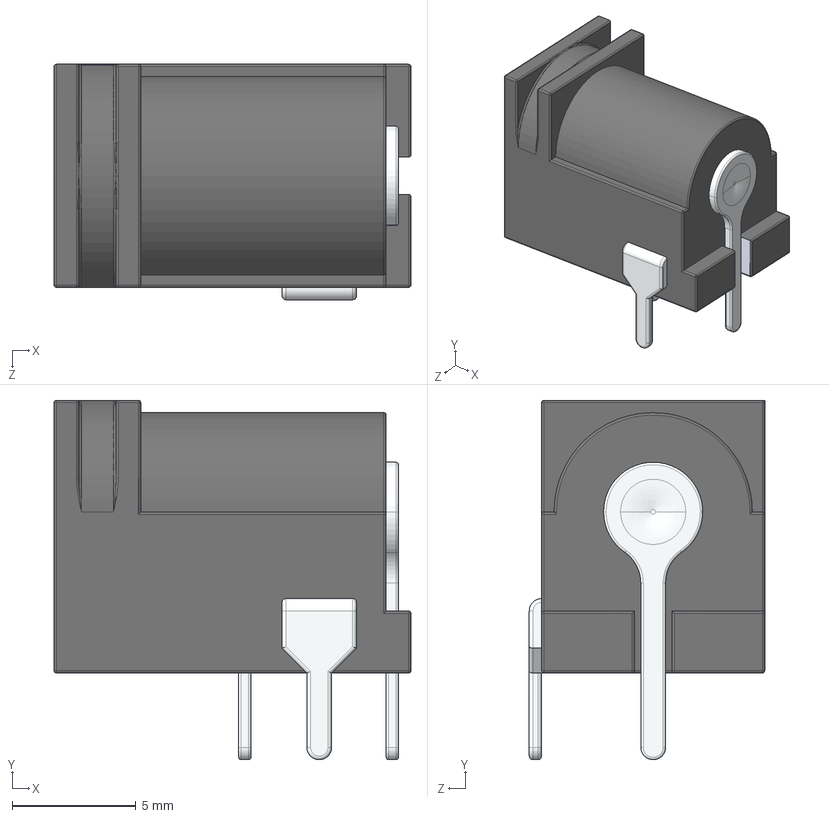
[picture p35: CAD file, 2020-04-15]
electronics/arduino/REES_V2_TRH_SMD/Modelos 3D/User Library-DC_Jack-1.step
14.4 x 14.5 x 9.50 mm

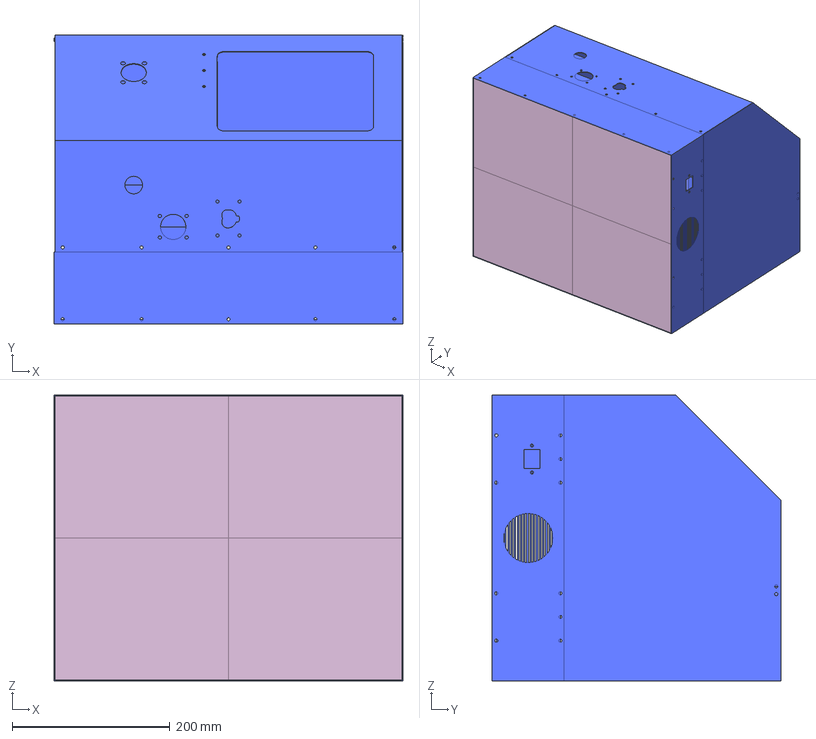
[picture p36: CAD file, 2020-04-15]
files/cut/chapa/bmr_000_completo_para_fabricar.igs
442.0 x 366.0 x 362.0 mm

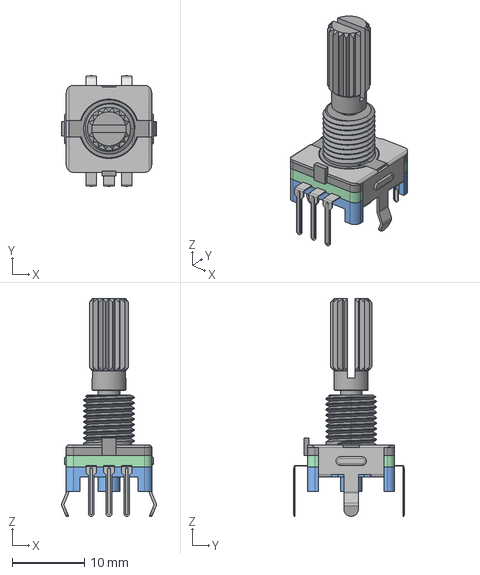
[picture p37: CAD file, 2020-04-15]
electronics/arduino/REES_V2_TRH_SMD/Modelos 3D/EC11_Rotary_Encoder_Switched.step
13.1 x 15.3 x 30.1 mm

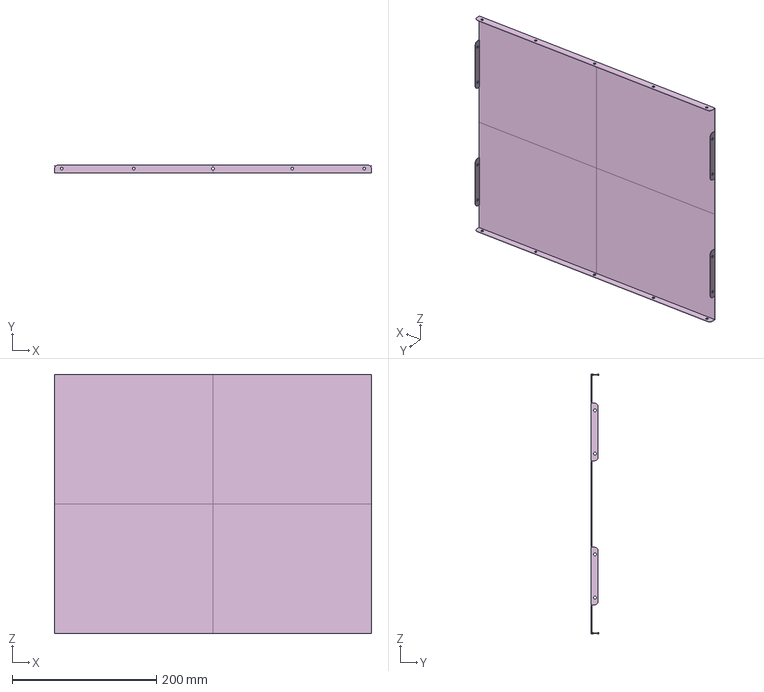
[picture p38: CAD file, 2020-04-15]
files/cut/chapa/bmr_002_tapa_culo_para_fabricar.igs
440.0 x 11.0 x 360.0 mm

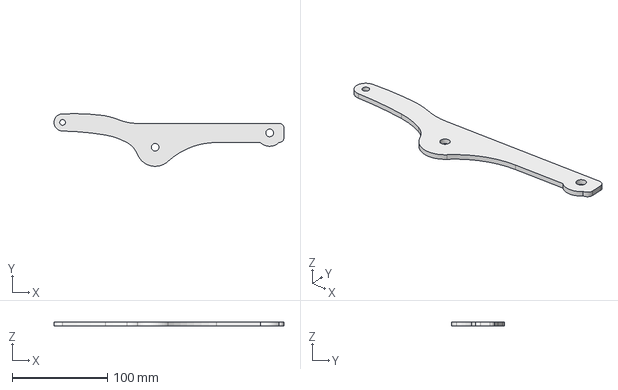
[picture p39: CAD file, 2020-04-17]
files/cut/corte/Version_2/STP/Balancin_v2.step
241.0 x 55.2 x 4.00 mm

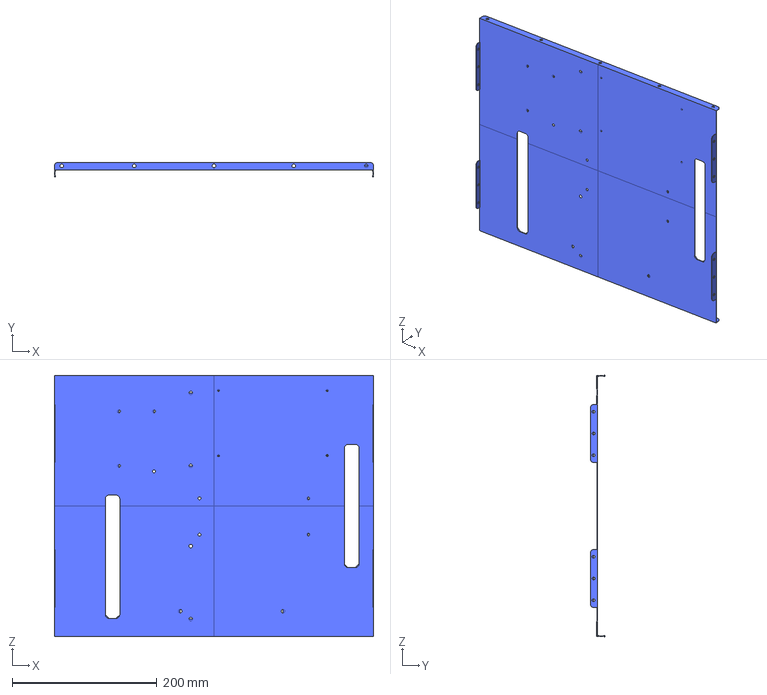
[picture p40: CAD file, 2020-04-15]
files/cut/chapa/bmr_007_culo_cubierta_para_fabricar.igs
440.0 x 20.0 x 360.0 mm

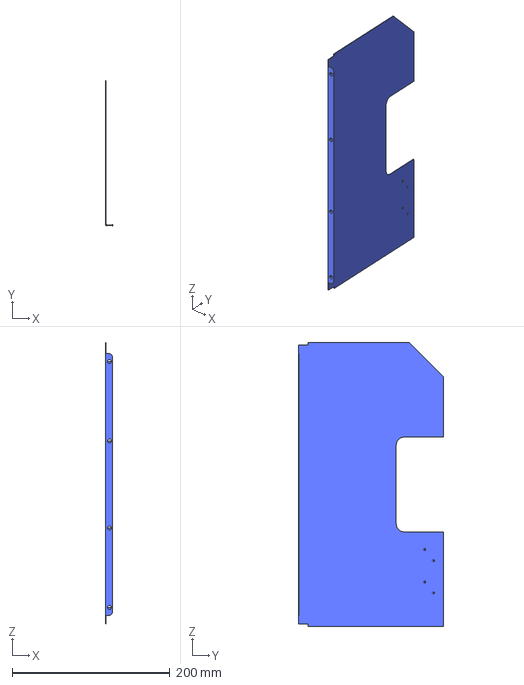
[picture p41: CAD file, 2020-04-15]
files/cut/chapa/bmr_004_separador_inferior_para_fabricar.igs
9.00 x 184.0 x 360.0 mm

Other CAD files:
files/cut/corte/Version_2/STP/Pala_v2.step
files/cut/chapa/bmr_001_carcasa_superior_para_fabricar.igs
files/cut/chapa/bmr_003_anillo_culo_para_fabricar_sin_rejilla.igs
files/cut/chapa/bmr_005_separador_superior_para_fabricar.igs
electronics/arduino/REES_V2_TRH_SMD/Modelos 3D/022057038.stp
electronics/arduino/REES_V2_TRH_SMD/Modelos 3D/022057048.stp
electronics/arduino/REES_V2_TRH_SMD/Modelos 3D/22057028.stp
electronics/arduino/REES_V2_TRH_SMD/Modelos 3D/User Library-128x64I2COLEDDisplayAdafruit.step
files/cut/chapa/bmr_008_taladros_ventilador_cajon_inferior.igs
files/cut/corte/Version_1/DXF/Balancin.dxf
files/cut/corte/Version_1/DXF/Base.dxf
files/cut/corte/Version_1/DXF/Frontal.dxf
files/cut/corte/Version_1/DXF/Lateral_D.dxf
files/cut/corte/Version_1/DXF/Lateral_I.dxf
files/cut/corte/Version_1/DXF/Leva.dxf
files/cut/corte/Version_1/DXF/Panel_beaglebone.dxf
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

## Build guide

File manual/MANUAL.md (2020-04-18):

## Manual de instrucciones

**Abreviaturas**

+ PIP (Peak Inspiratory Pressure), aplicación de una presión positiva al patrón de ventilación espontánea normal. Es una respiración espontánea con PEEP. Es una modalidad de soporte parcial.
+ PEEP (Positive End-Expiratory Pressure), técnica mecánica que se utiliza al ventilar a un paciente. Dicha técnica incluye el agregado de una cantidad de presión en los pulmones al final de cada respiración.
+ FR, Frecuencia de trabajo del respirador
+ VOL, volumen pulmonar de trabajo.

## Introducción
*El sistema Reespirator 2020 se puede construir en diferentes versiones por tanto su uso también difiere un poco en función del modelo.*

Las últimas versiones cuentan con un interfaz de usuario táctil, simple y de sencillo manejo gracias a los botones de gran tamaño, que permiten controlar los parámetros de operativa en las diferentes situaciones que así lo requieran, aunque no es un requisito para hacer funcionar el dispositivo, los médicos agradecen la posibilidad de visualizar la forma de las ondas de funcionamiento del mismo, por eso se ha implementado también la opción de monitorizar dichas señales en un ordenador o dispositivo externo conectado por puerto serie, cuando no se puede utilizar una pantalla integrada en el dispositivo.

Por eso está prevista la utilización de uno o varios encoder y algunos botones dónde la opción de la pantalla sea más complicada de conseguir, pero manteniendo la opción de visualización externa comentada.

En los siguientes apartados del presente documento se muestran en detalle las opciones de operativa de Reespirator 2020 para cada una de las dos versiones:

* [Manual de usuario del modelo Arduino](https://gitlab.com/reespirator/reespirator2020/-/blob/master/manual/MANUAL-ARDUINO.md "Manual de Reespirator 2020 - modelo Arduino")

* [Manual de usario del modelo con PLC Siemens](https://gitlab.com/reespirator/reespirator2020/-/blob/master/manual/MANUAL-PLC.md "Manual de Reespirator 2020 - modelo PLC")

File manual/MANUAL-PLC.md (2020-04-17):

## Manual de usuario de Reespirator 2020 - Modelo PLC ## 

**Interfaz de usuario**

En el modelo de Reespirator 2020 con PLC en el caso de usar un autómata de Siemens S7-1200, este se complementa con un HMI (Human-Machine Interface), una pantalla táctil que permite visualizar e interactuar con las funciones del dispositivo.

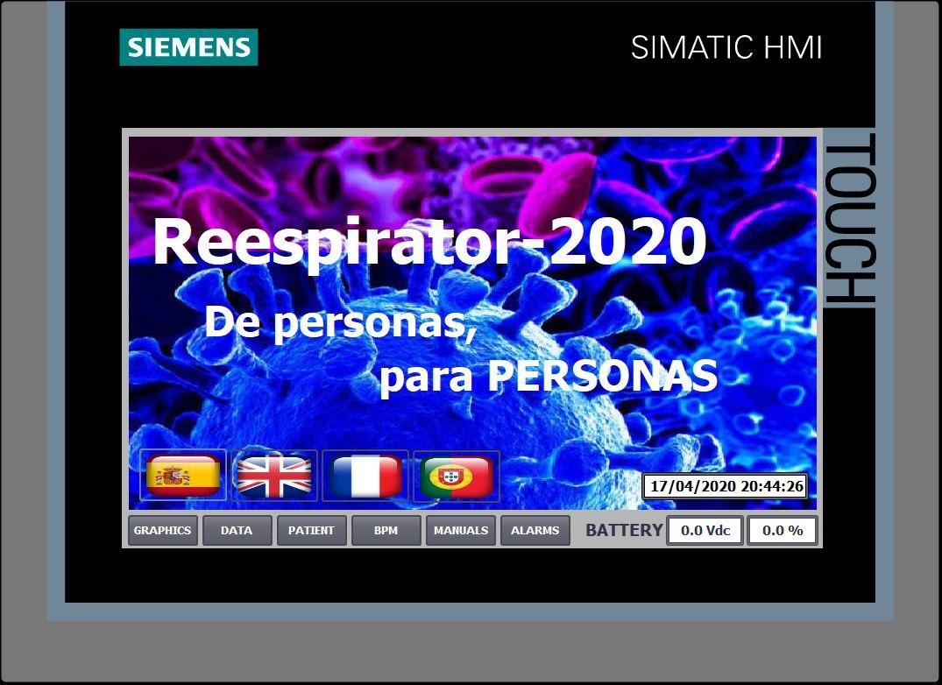
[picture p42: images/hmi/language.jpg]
Pantalla de inicio Pantalla de inicio de Reespirator 2020


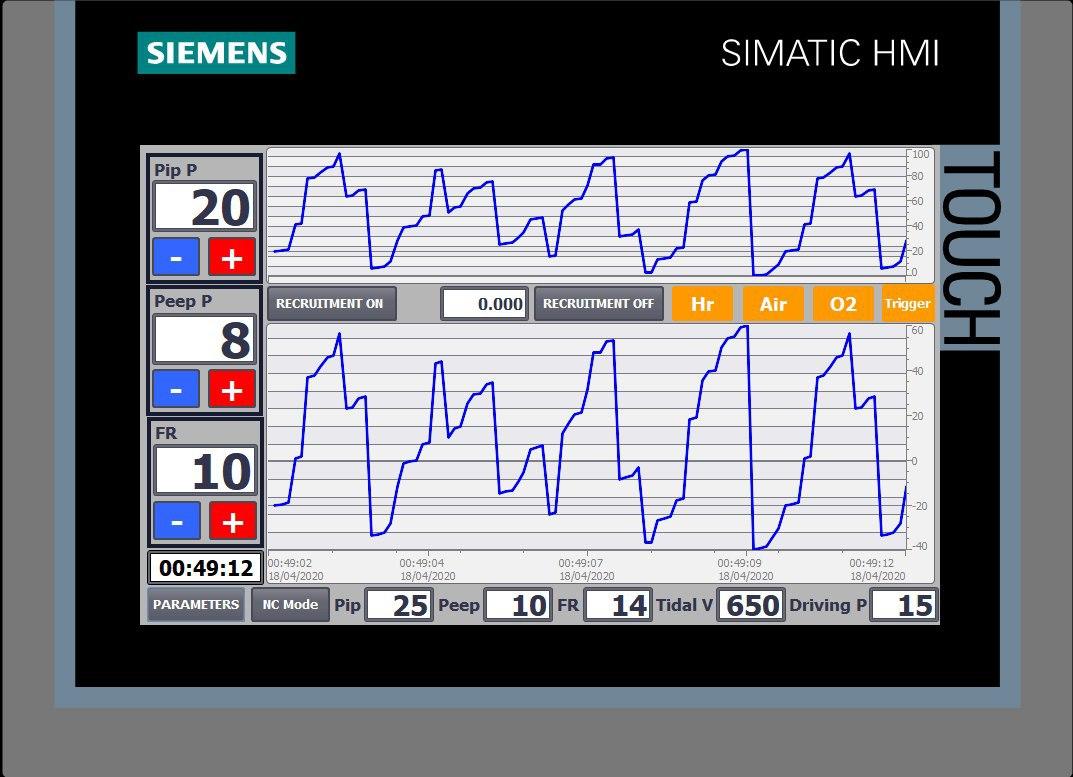
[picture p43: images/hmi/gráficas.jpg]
Gráficas Pantalla de gráficas


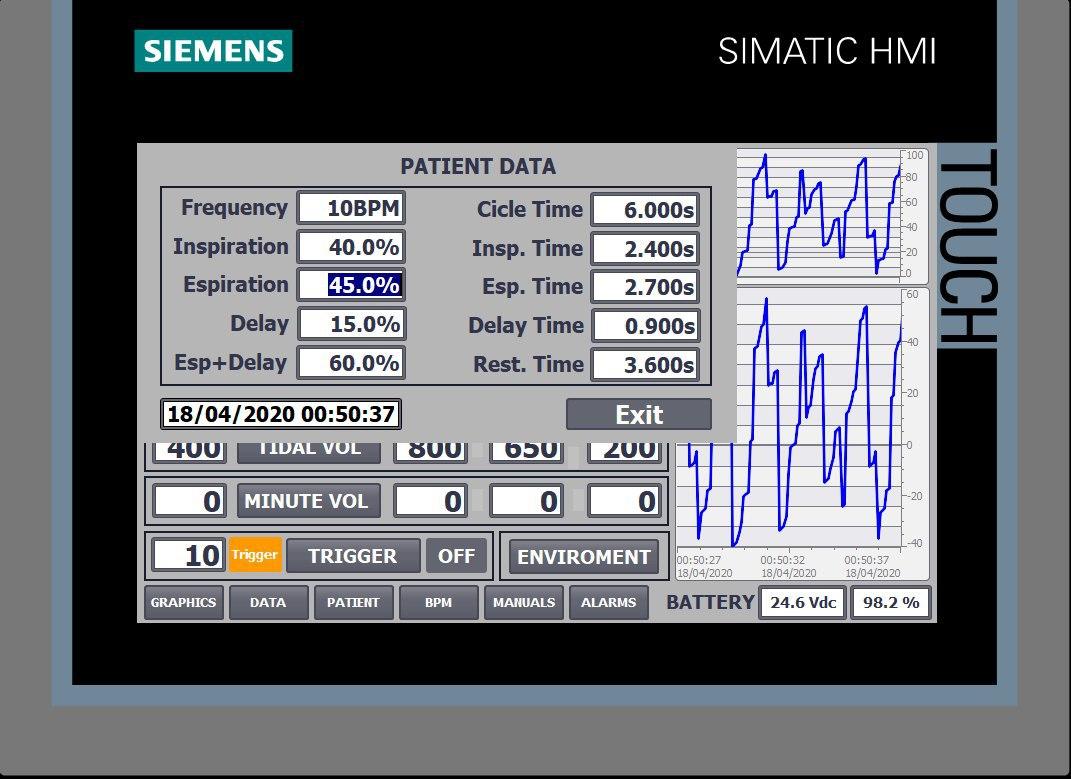
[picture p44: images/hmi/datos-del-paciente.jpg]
Datos del paciente


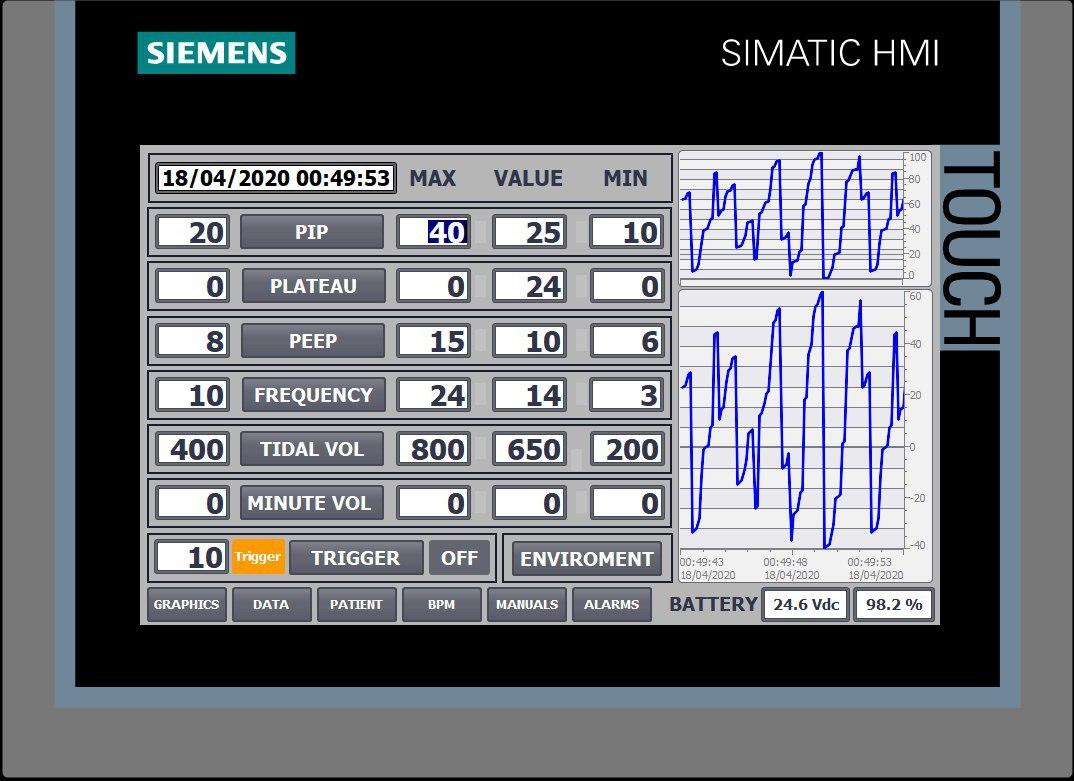
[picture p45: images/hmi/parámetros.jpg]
Parámetros


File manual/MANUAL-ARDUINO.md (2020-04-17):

## Manual de usuario de Reespirator 2020 - Modelo Arduino ## 

**Interfaz de usuario**

Como se ha indicado en el apartado introductorio del presente documento, el interfaz de usuario de Reespirator 2020 cuenta con una botonera de gran tamaño para permitir realizar las acciones que se requieran por el equipo médico. Adicionalmente, existen dos grandes apartados dentro de la ventana de trabajo:

* Visualización gráfica de estado, permite visualizar la progresión de los parámetros de flujo y presión del respirador.
* Ventana de información, muestra, dependiendo de la opción pulsada:
    - La información actual de trabajo del respirador
    - Los parámetros de configuración del respirador

Las siguientes capturas de pantalla muestran estos bloques claramente diferenciados:

    Interfaz de Usuario de Reespirator 2020 con información de trabajo

    Interfaz de Usuario de Reespirator 2020 con parámetros de configuración

## Menú de navegación
El menú de opciones de Reespirator cuenta únicamente con dos botones de acción:
* **INICIO**: muestra los valores numéricos de presión, flujo y volumen en tiempo real.
* **CONF**: muestra los parámetros de configuración de Reespirator 

# Parámetros de configuración
Pulsando sobre el botón **CONF** se visualizan los parámetros de configuración de
Reespirator, los cuales se indican a continuación:
* **PIP** (cmH2O), permite establecer el valor de trabajo. El rango comprendido está entre 1 y 79
* **PEEP** (cmH2O), al igual que el caso de PIP, establece el valor de trabajo con un rango comprendido entre 0 y 78, teniendo que ser siempre menor que el valor de PIP.
* **FR** (rpm), con un rango comprendido entre 1 y 30 permite establecer la frecuencia de trabajo.

# Información en tiempo real
Al iniciar Reespirator se muestran los valores de funcionamiento en tiempo real. Estos parámetros de funcionamiento, que se detallan a continuación, se refrescan cada 100 milisegundos:
* PIP (cmH2O). Peak Inspiratory Pressure
* PEEP (cmH2O). Positive End-Expiratory Pressure
* FR (rpm). Frecuencia de Trabajo
* VOL (ml). Cantidad de Aire con el que está trabajando Reespirator

Asimismo, en esta ventana de parámetros, se permite activar el Modo Recruit en el respirador, el cual permite realizar el aumento transitorio de la presión transpulmonar aplicada para reclutar alvéolos en el pulmón colapsado. Seguidamente se detalla el modo de trabajo en reespirator.

**Modo de reclutamiento**
Como ya se ha indicado, el modo Recruit permite realizar un aumento transitorio de la presión transpulmonar aplicada para re-airear el pulmón colapsado. Para activar esta funcionalidad, simplemente basta con tocar en la pantalla sobre el botón **RECRUIT**.
Tras activarse, el botón anteriormente presionado cambia a color rojo y el texto de este cambia a STOP RECRUIT,
para permitir detener la operación.
Debido al concepto de transitoriedad, en Reespirator el tiempo máximo de la operación de Recruit está configurado
a un máximo de 40 segundos. Es decir que si, transcurrido este tiempo no se desactiva manualmente, Reespirator lo hará automáticamente.

**Visualización gráfica**
Reespirator muestra de forma gráfica y en tiempo real los niveles de Presión y Flujo respectivamente. El tiempo total de ciclo que se muestra en ambas gráficas es de un minuto, tiempo suficiente para poder visualizar la evolución más reciente del paciente.
Los rangos de visualización de gráficas son:
+ Presión: entre 0 y 50 cmH2O
+ Flujo: entre -20 y 30 litros por minuto

Visualización de Gráficas de Presión y Flujo en Tiempo Real

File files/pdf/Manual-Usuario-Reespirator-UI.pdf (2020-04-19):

# Manual Usuario Reespirator UI

## Abreviaturas

- PIP (Peak Inspiratory Pressure), aplicación de una presión positiva al patrón de ventilación espontánea normal. Es una respiración espontánea con PEEP. Es una modalidad de soporte parcial.
- PEEP (Positive End-Expiratory Pressure), técnica mecánica que se utiliza al ventilar a un paciente. Dicha técnica incluye el agregado de una cantidad de presión en los pulmones al final de cada respiración.
- FR, Frecuencia de trabajo del respirador
- VOL, volumen pulmonar de trabajo.

## Introducción

El sistema Reespirator 23 cuenta con un interfaz de usuario táctil, simple y de sencillo manejo gracias a los botones de gran tamaño que permiten controlar los parámetros de operativa en las diferentes situaciones que así lo requieran.

Gracias a la orientación de la pantalla así como a la tonalidad y contraste empleados es posible supervisar el estado del paciente sin necesidad de estar muy cerca de este.

En los siguientes apartados del presente documento se muestran en detalle las opciones de operativa de Reespirator 23

## El interfaz de usuario

Como se ha indicado en el apartado introductorio del presente documento, el interfaz de usuario de Reespirator 23 cuenta con una botonera de gran tamaño para permitir realizar las acciones que se requieran por el equipo médico. Adicionalmente, existen dos grandes apartados dentro de la ventana de trabajo:

- Visualización gráfica de estado, permite visualizar la progresión de los parámetros de flujo y presión del respirador
- Ventana de Información, muestra, dependiendo de la opción pulsada:
- La información actual de trabajo del respirador
- Los parámetros de configuración del respirador

Las siguientes capturas de pantalla muestran estos bloques claramente diferenciados:

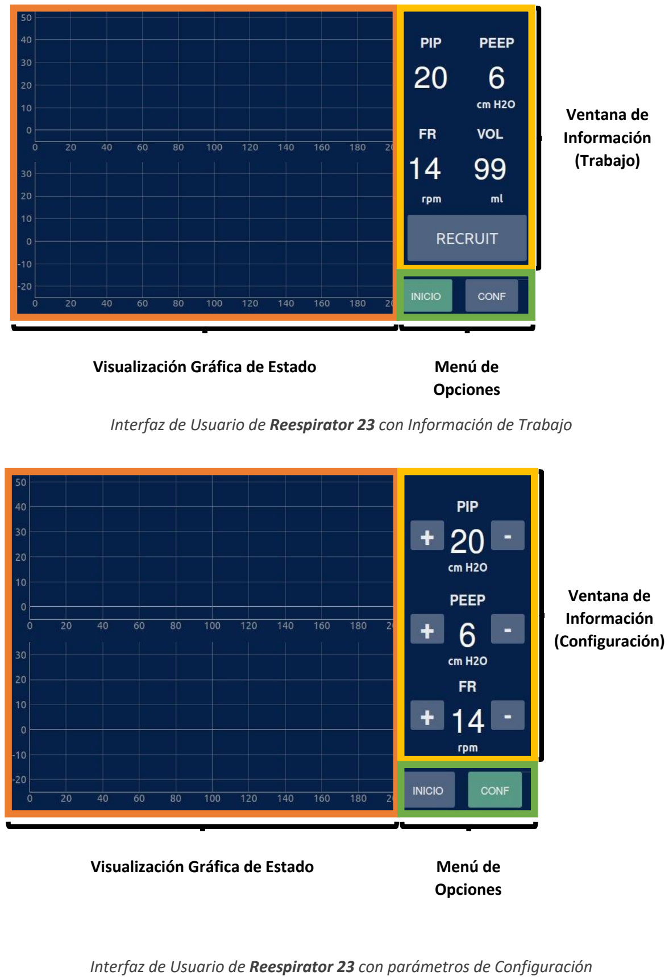
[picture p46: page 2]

Interfaz de Usuario de Reespirator 23 con Información de Trabajo

Interfaz de Usuario de Reespirator 23 con parámetros de Configuración

Visualización Gráfica de Estado | Menú de Opciones

Ventana de
Información
(Trabajo)
Visualización Gráfica de Estado | Menú de Opciones

Ventana de
Información
(Configuración)

## Menú de Opciones

Gracias a su sencillez, el menú de opciones del Reespirator 23 cuenta únicamente con dos botones de acción:

- INICIO, permite iniciar el respirador
- CONF, muestra los parámetros de configuración de Reespirator 23

## Parámetros de Configuración

Pulsando sobre el botón CONFIG se visualizan los parámetros de configuración de Reespirator 23, los cuales se indican a continuación:

- PIP (cm H2O), permite establecer el valor de trabajo. El rango comprendido está entre 1 y 79
- PEEP (cm H2O), al igual que el caso de PIP, establece el valor de trabajo con un rango comprendido entre 0 y 78, teniendo que ser siempre menor que el valor de PIP.
- FR (rpm), con un rango comprendido entre 1 y 29 permite establecer la frecuencia de trabajo

## Información en tiempo real

Al iniciar Reespirator 23 se muestran los valores de funcionamiento en tiempo Real. Estos parámetros de funcionamiento, que se detallan a continuación, se refrescan cada 50 milisegundos:

•PIP (cm H2O). Peak Inspiratory Pressure
•PEEP (cm H2O). Positive End-Expiratory Pressure
•FR (rpm). Frecuencia de Trabajo
•VOL (ml). Cantidad de Aire con el que está trabajando Reespirator 23

Asimismo, en esta ventana de parámetros, se permite activar el Modo Recruit en el respirador, el cual permite realizar el aumento transitorio de la presión transpulmonar aplicada para reairear el pulmón colapsado. Seguidamente se detalla el modo de trabajo en reespirator.

### El modo Recruit

Como ya se ha indicado, el modo Recruit permite realizar un aumento transitorio de la presión transpulmonar aplicada para reairear el pulmón colapsado. Para activar esta funcionalidad, simplemente basta con tocar en la pantalla sobre el botón RECRUIT.

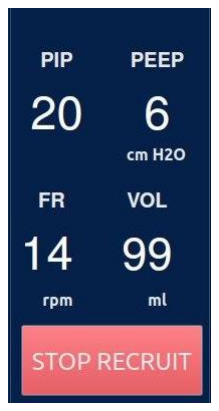
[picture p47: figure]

Tras activarse, el botón anteriormente presionado cambia a color rojo y el texto de este cambia a STOP RECRUIT, para permitir detener la operación.

Debido al concepto de transitoriedad, en Reespirator 23 el tiempo máximo de la operación de Recruit está configurado a un máximo de 40 segundos. Es decir que si, transcurrido este tiempo no se desactiva manualmente, Reespirator 23 lo hará automáticamente.

## Visualización gráfica

Reespirator 23 muestra de forma gráfica y en tiempo real los niveles de Presión y Flujo respectivamente. El tiempo total de ciclo que se muestra en ambas gráficas es de un minuto, tiempo suficiente para poder visualizar la evolución más reciente del paciente.

Los rangos de visualización de gráficas son:

- Presión: entre 0 y 50
- Flujo: entre -20 y 30

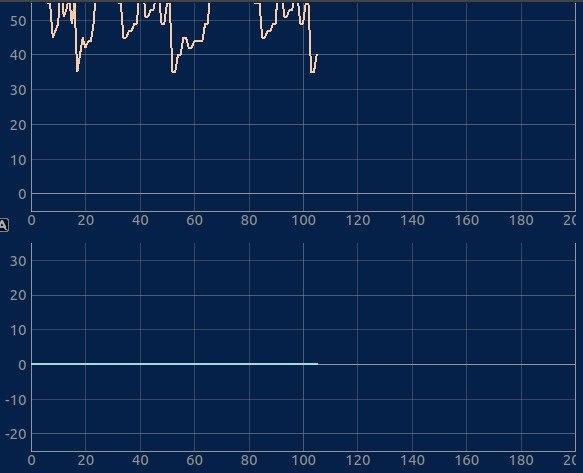
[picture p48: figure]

Visualización de Gráficas de Presión y Flujo en Tiempo Real

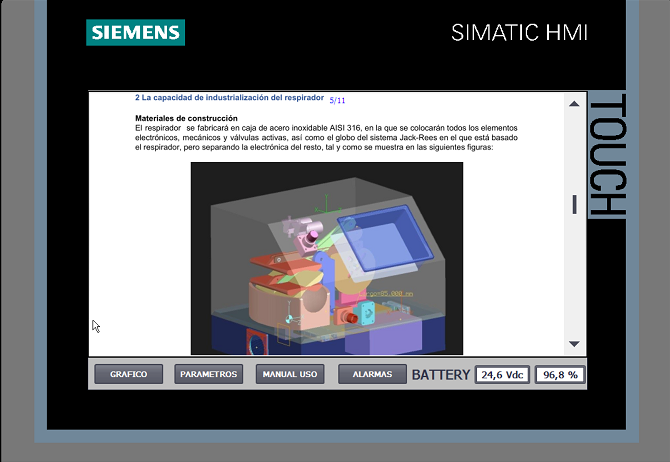
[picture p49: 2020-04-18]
images/hmi/manual-plc.png

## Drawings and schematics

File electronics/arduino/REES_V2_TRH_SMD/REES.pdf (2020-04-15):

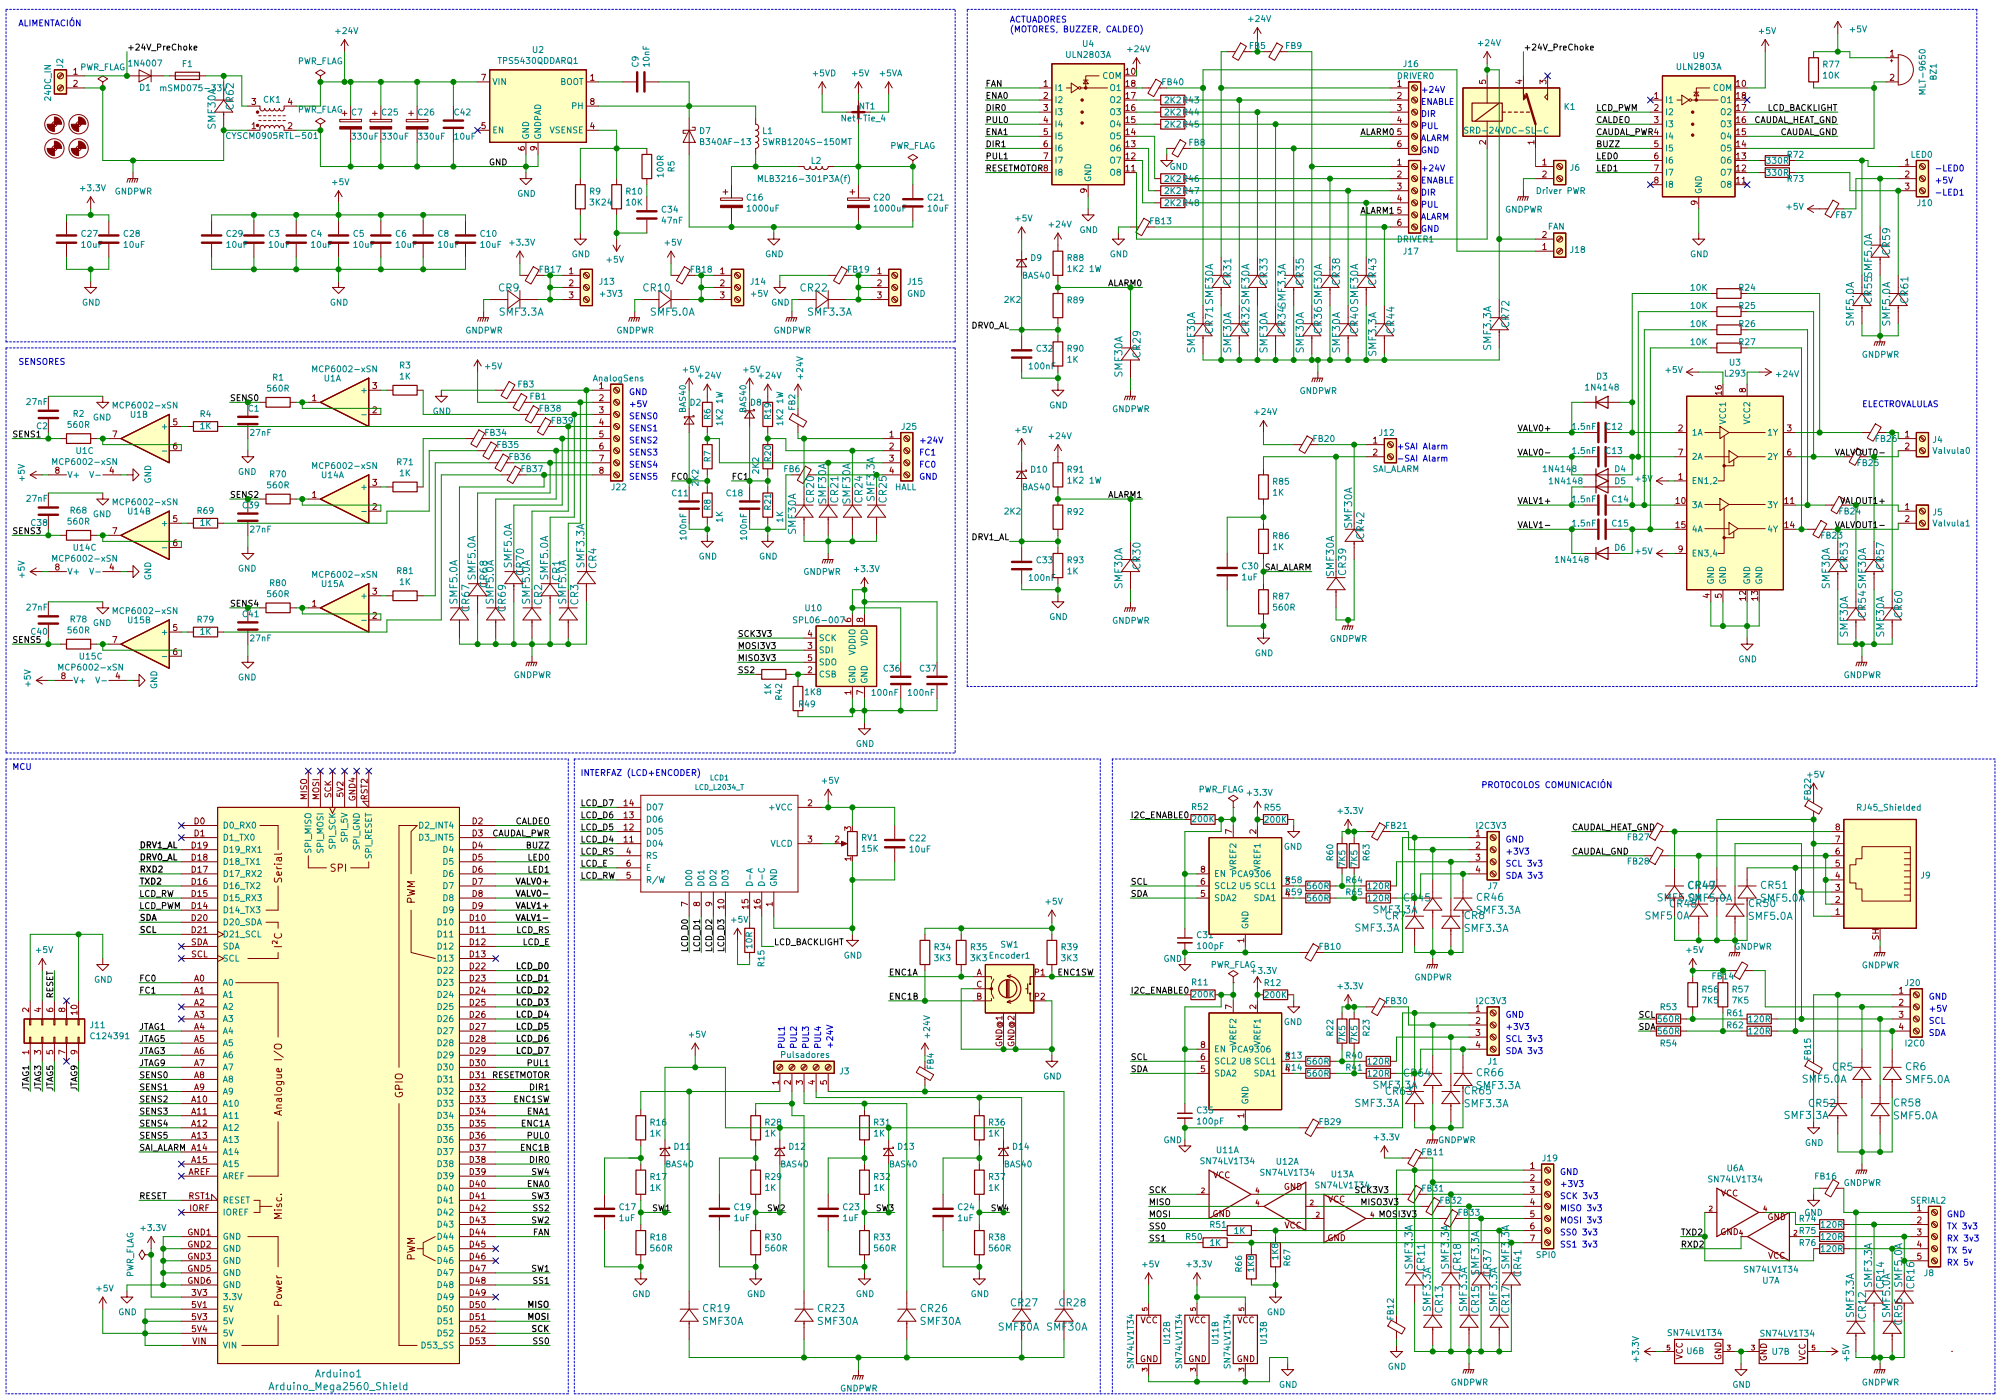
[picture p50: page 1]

ACTUADORES (MOTORES, BUZZER, CALDEO) ALIMENTACIÓN

1 CSB 2 SDI 3 SCK 4 SDO 5 VDDIO

INTERFAZ (LCD+ENCODER) MCU

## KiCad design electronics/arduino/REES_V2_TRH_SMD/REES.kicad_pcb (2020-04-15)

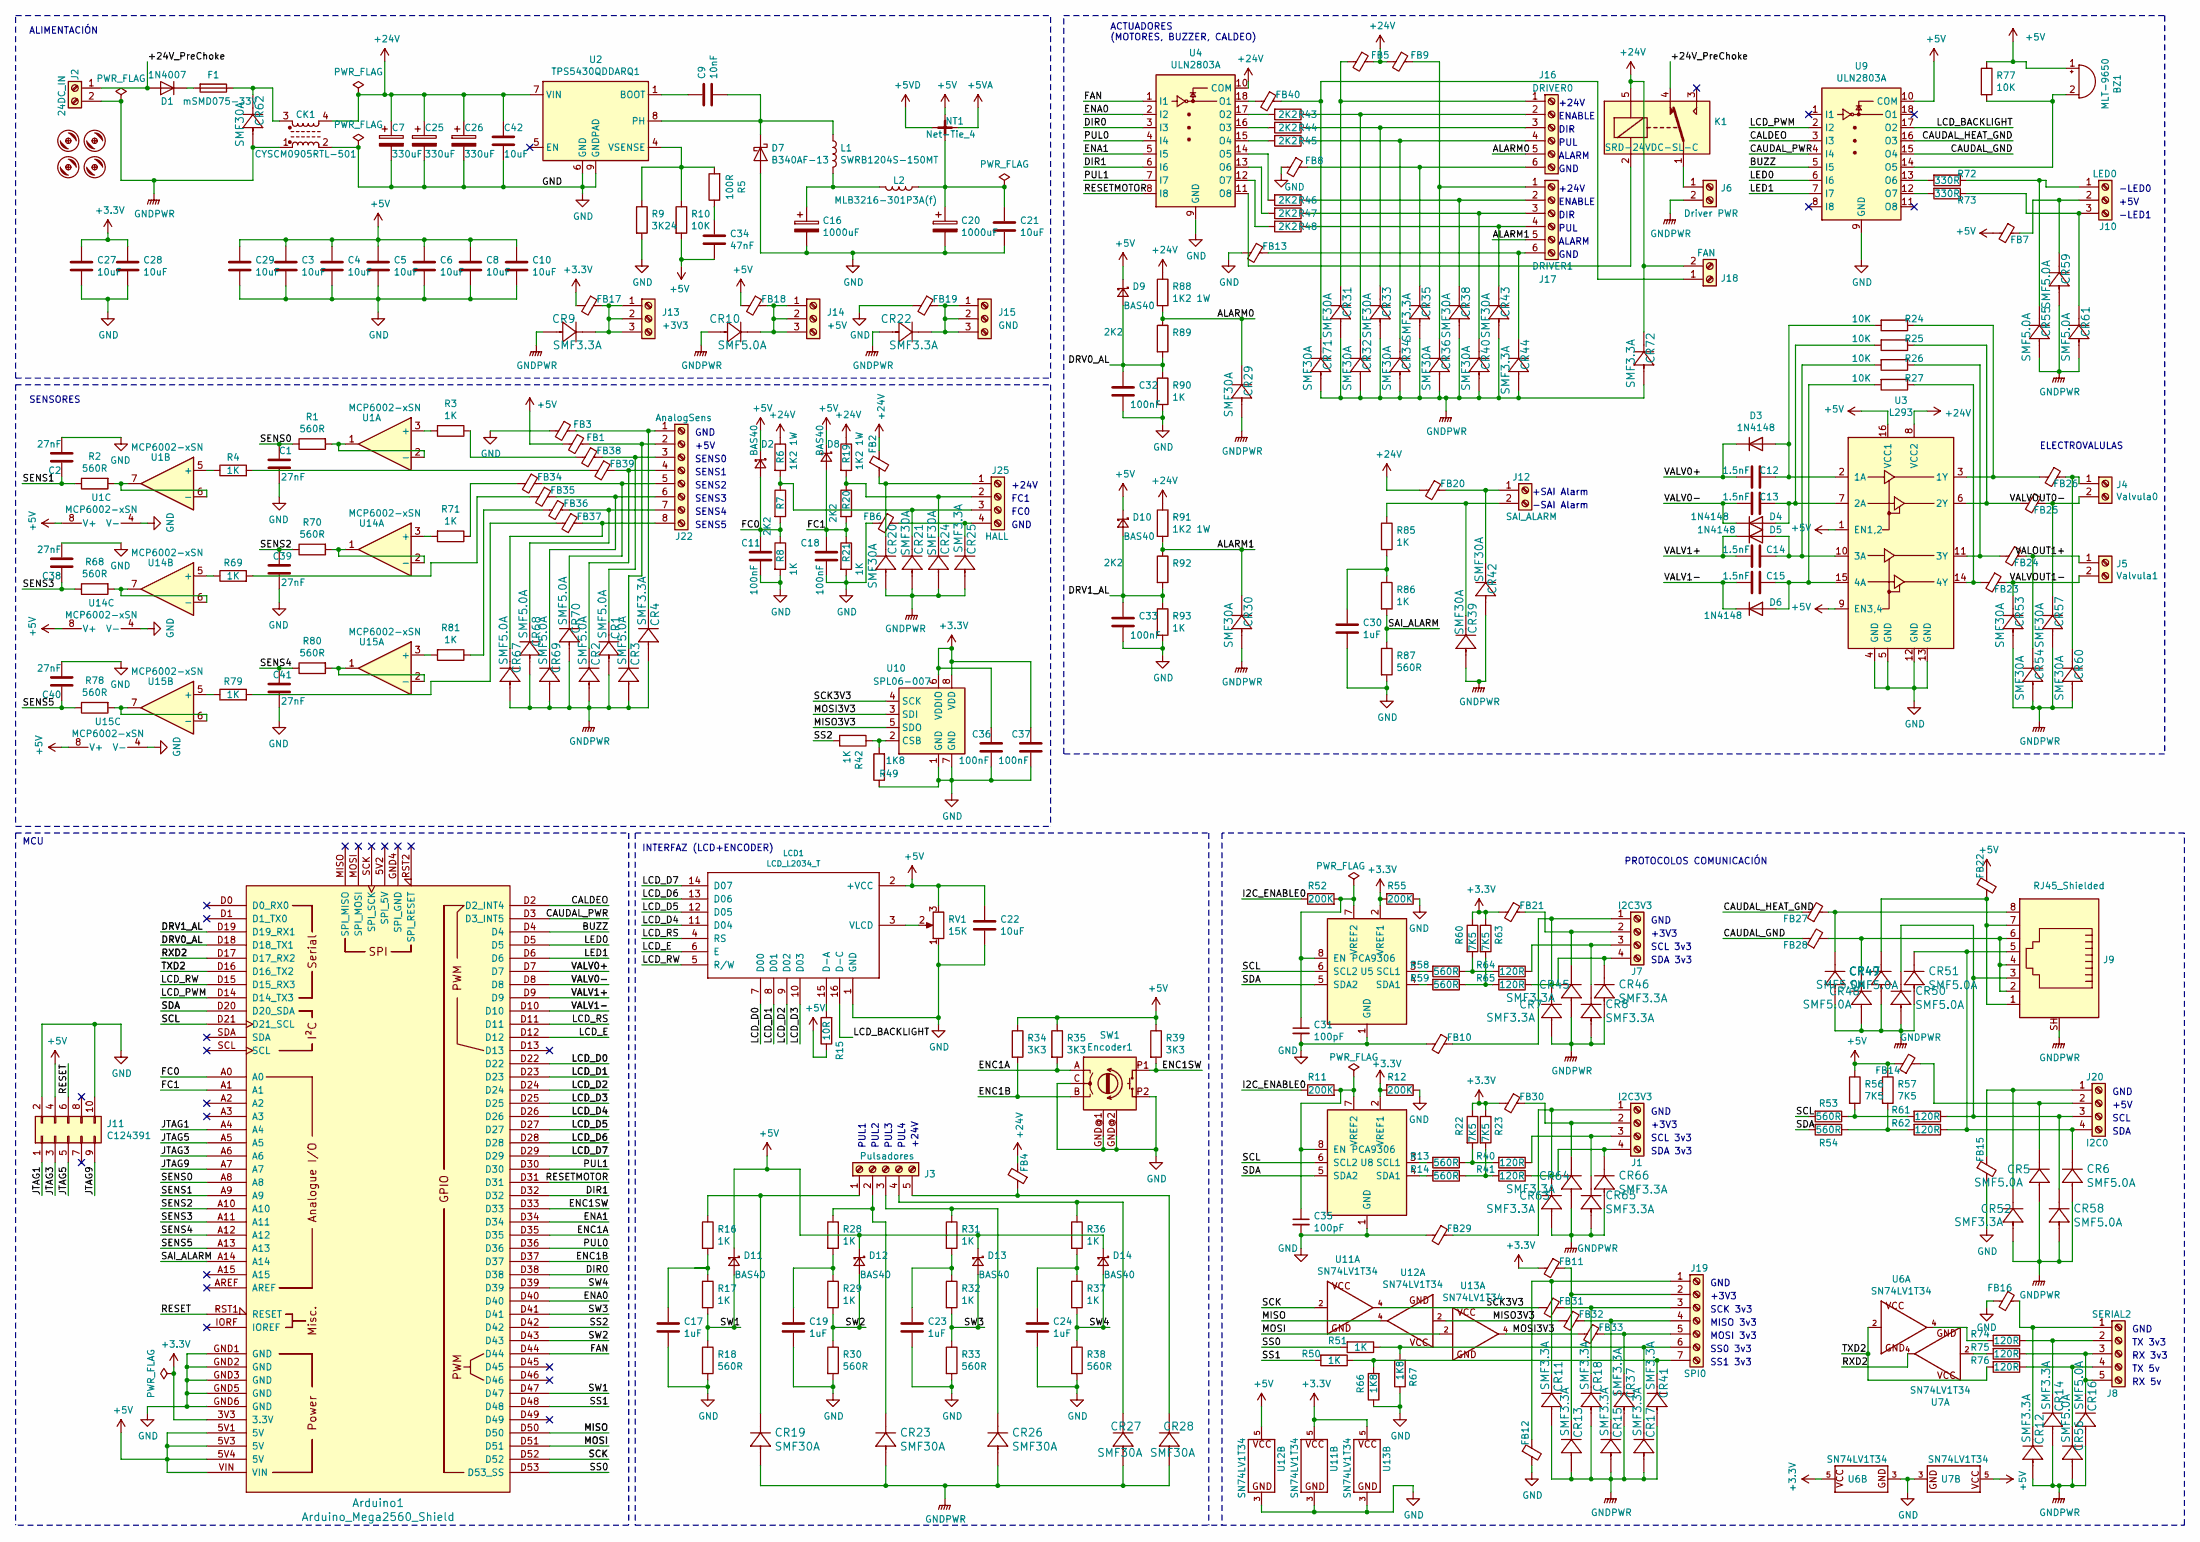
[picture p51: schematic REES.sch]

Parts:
Arduino1: Arduino_Mega2560_Shield
BZ1: MLT-9650; Buzzer_CUI_CPT-9019S-SMT
C1, C2, C38, C39, C40, C41: 27nF; C_0603_1608Metric
C3, C4, C5, C6, C8, C10, C21, C22, C27, C28, C29, C42: 10uF; C_1206_3216Metric
C7, C25, C26: 330uF; CP_Elec_10x10.5
C9: 10nF; C_0603_1608Metric
C11, C18, C32, C33, C36, C37: 100nF; C_0603_1608Metric
C12, C13, C14, C15: 1.5nF; C_0603_1608Metric
C16, C20: 1000uF; CP_Elec_10x10.5
C17, C19, C23, C24, C30: 1uF; C_0603_1608Metric
C31, C35: 100pF; C_0603_1608Metric
C34: 47nF; C_0603_1608Metric
CK1: CYSCM0905RTL-501; L_CommonMode_Wuerth_WE-SL2
CR1, CR2, CR3, CR5, CR6, CR10, CR16, CR47, CR48, CR49, CR50, CR51, CR55, CR56, CR58, CR59, CR61, CR67, CR68, CR69, CR70: SMF5.0A; D_SOD-123F
CR4, CR7, CR8, CR9, CR11, CR12, CR13, CR14, CR15, CR17, CR18, CR22, CR25, CR35, CR37, CR41, CR44, CR45, CR46, CR52, CR63, CR64, CR65, CR66, CR72: SMF3.3A; D_SOD-123F
CR19, CR20, CR21, CR23, CR24, CR26, CR27, CR28, CR29, CR30, CR31, CR32, CR33, CR34, CR36, CR38, CR39, CR40, CR42, CR43, CR53, CR54, CR57, CR60, CR62, CR71: SMF30A; D_SOD-123F
D1: 1N4007; D_SMA
D2, D8, D9, D10, D11, D12, D13, D14: BAS40; D_SOT-23_ANK
D3, D4, D5, D6: 1N4148; D_SOD-123
D7: B340AF-13; D_SMA
F1: mSMD075-33V; Fuse_1812_4532Metric
FB1, FB2, FB3, FB4, FB5, FB6, FB7, FB8, FB9, FB10, FB11, FB12, FB13, FB14, FB15, FB16, FB17, FB18, FB19, FB20, FB21, FB22, FB23, FB24, FB25, FB26, FB27, FB28, FB29, FB30, FB31, FB32, FB33, FB34, FB35, FB36, FB37, FB38, FB39, FB40: MLB3216-301P3A(f); C_1206_3216Metric
H1, H2, H3, H4: HOLES_MOUNT-HOLE3.6; HOLES_3,6
J1, J7: I2C3V3; TerminalBlock_Phoenix_MKDS-3-4-5.08_1x04_P5.08mm_Horizontal
J2: 24DC_IN; TerminalBlock_Phoenix_MKDS-3-2-5.08_1x02_P5.08mm_Horizontal
J3: Pulsadores; TerminalBlock_Phoenix_MKDS-3-5-5.08_1x05_P5.08mm_Horizontal
J4: Valvula0; TerminalBlock_Phoenix_MKDS-3-2-5.08_1x02_P5.08mm_Horizontal
J5: Valvula1; TerminalBlock_Phoenix_MKDS-3-2-5.08_1x02_P5.08mm_Horizontal
J6: Driver PWR; TerminalBlock_Phoenix_MKDS-3-2-5.08_1x02_P5.08mm_Horizontal
J8: SERIAL2; TerminalBlock_Phoenix_MKDS-3-5-5.08_1x05_P5.08mm_Horizontal
J9: RJ45_Shielded; RJ45_Hanrun_HR911105A
J10: LED0; TerminalBlock_Phoenix_MKDS-3-3-5.08_1x03_P5.08mm_Horizontal
J11: C124391; PinHeader_2x05_P2.54mm_Vertical_SMD
J12: SAI_ALARM; TerminalBlock_Phoenix_MKDS-3-2-5.08_1x02_P5.08mm_Horizontal
J13: +3V3; TerminalBlock_Phoenix_MKDS-3-3-5.08_1x03_P5.08mm_Horizontal
J14: +5V; TerminalBlock_Phoenix_MKDS-3-3-5.08_1x03_P5.08mm_Horizontal
J15: GND; TerminalBlock_Phoenix_MKDS-3-3-5.08_1x03_P5.08mm_Horizontal
J16: DRIVER0; TerminalBlock_Phoenix_MKDS-3-6-5.08_1x06_P5.08mm_Horizontal
J17: DRIVER1; TerminalBlock_Phoenix_MKDS-3-6-5.08_1x06_P5.08mm_Horizontal
J18: FAN; TerminalBlock_Phoenix_MKDS-3-2-5.08_1x02_P5.08mm_Horizontal
J19: SPI0; TerminalBlock_Phoenix_MKDS-3-7-5.08_1x07_P5.08mm_Horizontal
J20: I2C0; TerminalBlock_Phoenix_MKDS-3-4-5.08_1x04_P5.08mm_Horizontal
J22: AnalogSens; TerminalBlock_Phoenix_MKDS-3-8-5.08_1x08_P5.08mm_Horizontal
J25: HALL; TerminalBlock_Phoenix_MKDS-3-4-5.08_1x04_P5.08mm_Horizontal
K1: SRD-24VDC-SL-C; Relay_SPDT_Omron-G5LE-1
L1: SWRB1204S-150MT; L_Bourns_SRR1210A
L2: MLB3216-301P3A(f); C_1206_3216Metric
LCD1: LCD_L2034_T; L2034-T
NT1: Net-Tie_4; NetTie-4_SMD_Pad0.5mm
R1, R2, R13, R14, R18, R30, R33, R38, R53, R54, R58, R59, R68, R70, R78, R80, R87: 560R; R_0805_2012Metric
R3, R4, R8, R16, R17, R21, R28, R29, R31, R32, R36, R37, R42, R50, R51, R69, R71, R79, R81, R85, R86, R90, R93: 1K; R_1206_3216Metric
R5: 100R; R_0805_2012Metric
R6, R19, R88, R91: 1K2 1W; R_2512_6332Metric
R7, R20, R43, R44, R45, R46, R47, R48, R89, R92: 2K2; R_1206_3216Metric
R9: 3K24; R_0603_1608Metric
R10, R77: 10K; R_0603_1608Metric
R11, R12, R52, R55: 200K; R_0603_1608Metric
R15: 10R; R_1206_3216Metric
R22, R23, R56, R57, R60, R63: 7K5; R_0603_1608Metric
R24, R25, R26, R27: 10K; R_0805_2012Metric
R34, R35: 3K3; R_0603_1608Metric
R39: 3K3; R_0805_2012Metric
R40, R41, R61, R62, R64, R65, R74, R75, R76: 120R; R_1206_3216Metric
R49, R66, R67: 1K8; R_1206_3216Metric
R72, R73: 330R; R_0805_2012Metric
RV1: 15K; Potentiometer_Bourns_3214W_Vertical
SW1: Encoder1; PEC12_INCREMENTAL_ENCODER
U1, U14, U15: MCP6002-xSN; SOIC-8_3.9x4.9mm_P1.27mm
U2: TPS5430QDDARQ1; TI_SO-PowerPAD-8_ThermalVias
U3: L293; DIP-16_W7.62mm
U4, U9: ULN2803A; SOIC-18W_7.5x11.6mm_P1.27mm
U5, U8: PCA9306; TSSOP-8_3x3mm_P0.65mm
U6, U7, U11, U12, U13: SN74LV1T34; SOT-23-5_HandSoldering
U10: SPL06-007; Bosch_LGA-8_2x2.5mm_P0.65mm_ClockwisePinNumbering

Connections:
+3V3: Arduino1.3V3 (3.3V), C27.1, C28.1, C36.1, C37.1, FB11.2, FB17.2, FB21.2, FB30.2, R12.2, R22.1, R23.1, R55.2, R60.1, R63.1, U5.2 (VREF1), U6.5 (P$V+), U8.2 (VREF1), U10.6 (VDDIO), U10.8 (VDD), U11.5 (P$V+), U13.5 (P$V+)
+5V: Arduino1.5V1 (5V), Arduino1.5V3 (5V), Arduino1.5V4 (5V), Arduino1.VIN, BZ1.1 (-), C3.1, C4.1, C5.1, C6.1, C8.1, C10.1, C22.1, C29.1, C34.2, D2.1 (K), D8.1 (K), D9.1 (K), D10.1 (K), D11.1 (K), D12.1 (K), D13.1 (K), D14.1 (K), FB1.2, FB7.2, FB14.1, FB18.2, FB22.1, J11.4, LCD1.2 (+VCC), NT1.3, R10.2, R15.1, R34.1, R35.1, R39.1, R56.1, R57.1, R77.1, RV1.3, U1.8 (V+), U3.1 (EN1,2), U3.9 (EN3,4), U3.16 (VCC1), U7.5 (P$V+), U9.10 (COM), U12.5 (P$V+), U14.8 (V+), U15.8 (V+)
+24V: C7.1, C25.1, C26.1, C42.1, CK1.4, CR72.1, FB2.1, FB4.2, FB5.1, FB9.2, FB20.2, J18.2, K1.5, R6.1, R19.1, R88.1, R91.1, U2.7 (VIN), U3.8 (VCC2), U4.10 (COM)
/+24V_PreChoke: D1.2 (A), J2.1, K1.4
/ALARM0: CR29.1, J16.5, R88.2, R89.1
/ALARM1: CR30.1, J17.5, R91.2, R92.1
/BUZZ: Arduino1.D4, U9.5 (I5)
/CALDEO: Arduino1.D2 (D2_INT4), U9.3 (I3)
/CAUDAL_GND: FB28.1, U9.15 (O4)
/CAUDAL_HEAT_GND: FB27.1, U9.16 (O3)
/CAUDAL_PWR: Arduino1.D3 (D3_INT5), U9.4 (I4)
/DIR0: Arduino1.D38, U4.3 (I3)
/DIR1: Arduino1.D32, U4.6 (I6)
/DRV0_AL: Arduino1.D18 (D18_TX1), C32.1, D9.2 (A), R89.2, R90.1
/DRV1_AL: Arduino1.D19 (D19_RX1), C33.1, D10.2 (A), R92.2, R93.1
/ENA0: Arduino1.D40, U4.2 (I2)
/ENA1: Arduino1.D34, U4.5 (I5)
/ENC1A: Arduino1.D35, R35.2, SW1.A
/ENC1B: Arduino1.D37, R34.2, SW1.B
/ENC1SW: Arduino1.D33, R39.2, SW1.P1
/FAN: Arduino1.D44, U4.1 (I1)
/FC0: Arduino1.A0, C11.1, D2.2 (A), R7.2, R8.1
/FC1: Arduino1.A1, C18.1, D8.2 (A), R20.2, R21.1
/I2C_ENABLE0: R11.1, R52.1
/JTAG1: Arduino1.A4, J11.1
/JTAG3: Arduino1.A6, J11.3
/JTAG5: Arduino1.A5, J11.5
/JTAG9: Arduino1.A7, J11.9
/LCD_BACKLIGHT: LCD1.16 (D-C), U9.17 (O2)
/LCD_D0: Arduino1.D22, LCD1.7 (D00)
/LCD_D1: Arduino1.D23, LCD1.8 (D01)
/LCD_D2: Arduino1.D24, LCD1.9 (D02)
/LCD_D3: Arduino1.D25, LCD1.10 (D03)
/LCD_D4: Arduino1.D26, LCD1.11 (D04)
/LCD_D5: Arduino1.D27, LCD1.12 (D05)
/LCD_D6: Arduino1.D28, LCD1.13 (D06)
/LCD_D7: Arduino1.D29, LCD1.14 (D07)
/LCD_E: Arduino1.D12, LCD1.6 (E)
/LCD_PWM: Arduino1.D14 (D14_TX3), U9.2 (I2)
/LCD_RS: Arduino1.D11, LCD1.4 (RS)
/LCD_RW: Arduino1.D15 (D15_RX3), LCD1.5 (R/W)
/LED0: Arduino1.D5, U9.6 (I6)
/LED1: Arduino1.D6, U9.7 (I7)
/MISO: Arduino1.D50, U12.4 (Y)
/MISO3V3: FB32.2, U10.5 (SDO), U12.2 (A)
/MOSI: Arduino1.D51, U13.2 (A)
/MOSI3V3: FB33.2, U10.3 (SDI), U13.4 (Y)
/PUL0: Arduino1.D36, U4.4 (I4)
/PUL1: Arduino1.D30, U4.7 (I7)
/RESET: Arduino1.RST1 (RESET), J11.6
/RESETMOTOR: Arduino1.D31, U4.8 (I8)
/RXD2: Arduino1.D17 (D17_RX2), U7.4 (Y)
/SAI_ALARM: Arduino1.A14, R86.2, R87.1
/SCK: Arduino1.D52, U11.2 (A)
/SCK3V3: FB31.2, U10.4 (SCK), U11.4 (Y)
/SCL: Arduino1.D21 (D21_SCL), R53.2, U5.6 (SCL2), U8.6 (SCL2)
/SDA: Arduino1.D20 (D20_SDA), R54.2, U5.5 (SDA2), U8.5 (SDA2)
/SENS0: Arduino1.A8, C1.1, R1.1
/SENS1: Arduino1.A9, C2.1, R2.1
/SENS2: Arduino1.A10, C39.1, R70.1
/SENS3: Arduino1.A11, C38.1, R68.1
/SENS4: Arduino1.A12, C41.1, R80.1
/SENS5: Arduino1.A13, C40.1, R78.1
/SS0: Arduino1.D53 (D53_SS), R51.2
/SS1: Arduino1.D48, R50.2
/SS2: Arduino1.D42, R42.2
/SW1: Arduino1.D47, D11.2 (A), R17.2, R18.1
/SW2: Arduino1.D43, D12.2 (A), R29.2, R30.1
/SW3: Arduino1.D41, D13.2 (A), R32.2, R33.1
/SW4: Arduino1.D39, D14.2 (A), R37.2, R38.1
/TXD2: Arduino1.D16 (D16_TX2), R76.2, U6.2 (A)
/VALOUT1+: CR54.1, FB24.1, J5.1
/VALV0+: Arduino1.D7, C12.2, D3.1 (K)
/VALV0-: Arduino1.D8, C13.2, D4.1 (K)
/VALV1+: Arduino1.D9, C14.2, D5.1 (K)
/VALV1-: Arduino1.D10, C15.2, D6.1 (K)
/VALVOUT0-: CR57.1, FB25.1, J4.2
/VALVOUT1-: CR53.1, FB23.1, J5.2
GND: Arduino1.GND1 (GND), Arduino1.GND2 (GND), Arduino1.GND3 (GND), Arduino1.GND5 (GND), Arduino1.GND6 (GND), C1.2, C2.2, C3.2, C4.2, C5.2, C6.2, C7.2, C8.2, C10.2, C11.2, C16.2, C17.2, C18.2, C19.2, C20.2, C21.2, C22.2, C23.2, C24.2, C25.2, C26.2, C27.2, C28.2, C29.2, C30.2, C31.2, C32.2, C33.2, C35.2, C36.2, C37.2, C38.2, C39.2, C40.2, C41.2, C42.2, CK1.2, D7.2 (A), FB3.2, FB6.2, FB8.2, FB10.2, FB12.2, FB13.2, FB15.2, FB16.2, FB19.2, FB29.2, J11.2, J11.10, LCD1.1 (GND), R8.2, R9.2, R12.1, R18.2, R21.2, R30.2, R33.2, R38.2, R49.1, R55.1, R66.1, R67.1, R87.2, R90.2, R93.2, RV1.1, SW1.C, SW1.GND@1, SW1.GND@2, SW1.P2, U1.4 (V-), U2.6 (GND), U2.9 (GNDPAD), U3.4 (GND), U3.5 (GND), U3.12 (GND), U3.13 (GND), U4.9 (GND), U5.1 (GND), U6.3 (P$V-), U7.3 (P$V-), U8.1 (GND), U9.9 (GND), U10.1 (GND), U10.7 (GND), U11.3 (P$V-), U12.3 (P$V-), U13.3 (P$V-), U14.4 (V-), U15.4 (V-)
GNDPWR: CK1.1, CR1.2, CR2.2, CR3.2, CR4.2, CR5.2, CR6.2, CR7.2, CR8.2, CR9.2, CR10.2, CR11.2, CR12.2, CR13.2, CR14.2, CR15.2, CR16.2, CR17.2, CR18.2, CR19.2, CR20.2, CR21.2, CR22.2, CR23.2, CR24.2, CR25.2, CR26.2, CR27.2, CR28.2, CR29.2, CR30.2, CR31.2, CR32.2, CR33.2, CR34.2, CR35.2, CR36.2, CR37.2, CR38.2, CR39.2, CR40.2, CR41.2, CR42.2, CR43.2, CR44.2, CR45.2, CR46.2, CR47.2, CR48.2, CR49.2, CR50.2, CR51.2, CR52.2, CR53.2, CR54.2, CR55.2, CR56.2, CR57.2, CR58.2, CR59.2, CR60.2, CR61.2, CR62.2, CR63.2, CR64.2, CR65.2, CR66.2, CR67.2, CR68.2, CR69.2, CR70.2, CR71.2, CR72.2, J2.2, J6.2, J9.SH
unnamed: BZ1.2 (+), R77.2, U9.14 (O5)
unnamed: C9.1, U2.1 (BOOT)
unnamed: C9.2, D7.1 (K), L1.1, U2.8 (PH)
unnamed: C12.1, D3.2 (A), R24.2, U3.2 (1A)
unnamed: C13.1, D4.2 (A), R25.2, U3.7 (2A)
unnamed: C14.1, D5.2 (A), R26.2, U3.10 (3A)
unnamed: C15.1, D6.2 (A), R27.2, U3.15 (4A)
unnamed: C16.1, L1.2, L2.2
unnamed: C17.1, R16.2, R17.1
unnamed: C19.1, R28.2, R29.1
unnamed: C20.1, C21.1, L2.1, NT1.4
unnamed: C23.1, R31.2, R32.1
unnamed: C24.1, R36.2, R37.1
unnamed: C30.1, R85.2, R86.1
unnamed: C31.1, R52.2, U5.7 (VREF2), U5.8 (EN)
unnamed: C34.1, R5.1
unnamed: C35.1, R11.2, U8.7 (VREF2), U8.8 (EN)
unnamed: CK1.3, CR62.1, F1.1
unnamed: CR1.1, FB38.1, J22.3
unnamed: CR2.1, FB39.1, J22.4
unnamed: CR3.1, FB1.1, J22.2
unnamed: CR4.1, FB3.1, J22.1
unnamed: CR5.1, FB14.2, J20.2
unnamed: CR8.1, J7.3, R64.1
unnamed: CR9.1, FB17.1, J13.1, J13.2, J13.3
unnamed: CR10.1, FB18.1, J14.1, J14.2, J14.3
unnamed: CR11.1, FB12.1, J19.1
unnamed: CR12.1, FB16.1, J8.1
unnamed: CR13.1, FB11.1, J19.2
unnamed: CR14.1, J8.2, R74.1
unnamed: CR15.1, FB32.1, J19.4
unnamed: CR16.1, J8.3, J8.5, R75.1
unnamed: CR17.1, J19.6, R51.1, R67.2
unnamed: CR18.1, FB31.1, J19.3
unnamed: CR19.1, J3.1, R16.1
unnamed: CR20.1, FB2.2, J25.1
unnamed: CR21.1, J25.3, R6.2, R7.1
unnamed: CR22.1, FB19.1, J15.1, J15.2, J15.3
unnamed: CR23.1, J3.2, R28.1
unnamed: CR24.1, J25.2, R19.2, R20.1
unnamed: CR25.1, FB6.1, J25.4
unnamed: CR26.1, J3.3, R31.1
unnamed: CR27.1, J3.4, R36.1
unnamed: CR28.1, FB4.1, J3.5
unnamed: CR31.1, FB5.2, J16.1
unnamed: CR32.1, J16.2, R43.1
unnamed: CR33.1, J16.3, R44.1
unnamed: CR34.1, J16.4, R45.1
unnamed: CR35.1, FB8.1, J16.6
unnamed: CR36.1, FB9.1, J17.1
unnamed: CR37.1, FB33.1, J19.5
unnamed: CR38.1, J17.2, R46.1
unnamed: CR39.1, J12.2, R85.1
unnamed: CR40.1, J17.3, R47.1
unnamed: CR41.1, J19.7, R50.1, R66.2
unnamed: CR42.1, FB20.1, J12.1
unnamed: CR43.1, J17.4, R48.1
unnamed: CR44.1, FB13.1, J17.6
unnamed: CR45.1, FB21.1, J7.2
unnamed: CR7.1, CR46.1, FB10.1, J7.1, J7.4, R65.1
unnamed: CR47.1, FB27.2, J9.8
unnamed: CR48.1, FB28.2, J9.2, J9.4, J9.6
unnamed: CR49.1, FB22.2, J9.1, J9.7
unnamed: CR50.1, CR58.1, J9.3, J20.3, R61.1
unnamed: CR6.1, CR51.1, J9.5, J20.4, R62.1
unnamed: CR52.1, FB15.1, J20.1
unnamed: CR55.1, J10.1, R72.1
unnamed: CR56.1, J8.4, R76.1
unnamed: CR59.1, FB7.1, J10.2
unnamed: CR60.1, FB26.1, J4.1
unnamed: CR61.1, J10.3, R73.1
unnamed: CR63.1, CR66.1, FB29.1, J1.1, J1.4, R41.1
unnamed: CR64.1, FB30.1, J1.2
unnamed: CR65.1, J1.3, R40.1
unnamed: CR67.1, FB37.1, J22.8
unnamed: CR68.1, FB36.1, J22.7
unnamed: CR69.1, FB35.1, J22.6
unnamed: CR70.1, FB34.1, J22.5
unnamed: CR71.1, FB40.1, J18.1
unnamed: D1.1 (K), F1.2
unnamed: FB23.2, R27.1, U3.14 (4Y)
unnamed: FB24.2, R26.1, U3.11 (3Y)
unnamed: FB25.2, R25.1, U3.6 (2Y)
unnamed: FB26.2, R24.1, U3.3 (1Y)
unnamed: FB34.2, R71.1
unnamed: FB35.2, R69.2
unnamed: FB36.2, R81.1
unnamed: FB37.2, R79.2
unnamed: FB38.2, R3.1
unnamed: FB39.2, R4.2
unnamed: FB40.2, U4.18 (O1)
unnamed: J6.1, K1.1
unnamed: K1.2, U4.11 (O8)
unnamed: LCD1.3 (VLCD), RV1.2
unnamed: LCD1.15 (D-A), R15.2
unnamed: R1.2, U1.1, U1.2 (-)
unnamed: R2.2, U1.6 (-), U1.7
unnamed: R3.2, U1.3 (+)
unnamed: R4.1, U1.5 (+)
unnamed: R5.2, R9.1, R10.1, U2.4 (VSENSE)
unnamed: R13.1, R22.2, R40.2
unnamed: R13.2, U8.3 (SCL1)
unnamed: R14.1, R23.2, R41.2
unnamed: R14.2, U8.4 (SDA1)
unnamed: R42.1, R49.2, U10.2 (CSB)
unnamed: R43.2, U4.17 (O2)
unnamed: R44.2, U4.16 (O3)
unnamed: R45.2, U4.15 (O4)
unnamed: R46.2, U4.14 (O5)
unnamed: R47.2, U4.13 (O6)
unnamed: R48.2, U4.12 (O7)
unnamed: R53.1, R56.2, R61.2
unnamed: R54.1, R57.2, R62.2
unnamed: R58.1, R60.2, R64.2
unnamed: R58.2, U5.3 (SCL1)
unnamed: R59.1, R63.2, R65.2
unnamed: R59.2, U5.4 (SDA1)
unnamed: R68.2, U14.6 (-), U14.7
unnamed: R69.1, U14.5 (+)
unnamed: R70.2, U14.1, U14.2 (-)
unnamed: R71.2, U14.3 (+)
unnamed: R72.2, U9.13 (O6)
unnamed: R73.2, U9.12 (O7)
unnamed: R74.2, U6.4 (Y)
unnamed: R75.2, U7.2 (A)
unnamed: R78.2, U15.6 (-), U15.7
unnamed: R79.1, U15.5 (+)
unnamed: R80.2, U15.1, U15.2 (-)
unnamed: R81.2, U15.3 (+)

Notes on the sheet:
ALIMENTACIÓN
ACTUADORES (MOTORES, BUZZER, CALDEO)
SENSORES
PROTOCOLOS COMUNICACIÓN
MCU
ELECTROVALULAS
RX 5v
TX 5v
TX 3v3
GND
-SAI Alarm
+SAI Alarm
RX 3v3
SCL 3v3
SDA 3v3
+3V3
SDA
+5V
SCL
PUL
ENABLE
+24V
DIR
ALARM
-LED0
-LED1
PUL3
PUL1
PUL2
PUL4
SCK 3v3
MISO 3v3
MOSI 3v3
SS0 3v3
SS1 3v3
SENS1
SENS0
FC0
FC1
INTERFAZ (LCD+ENCODER)

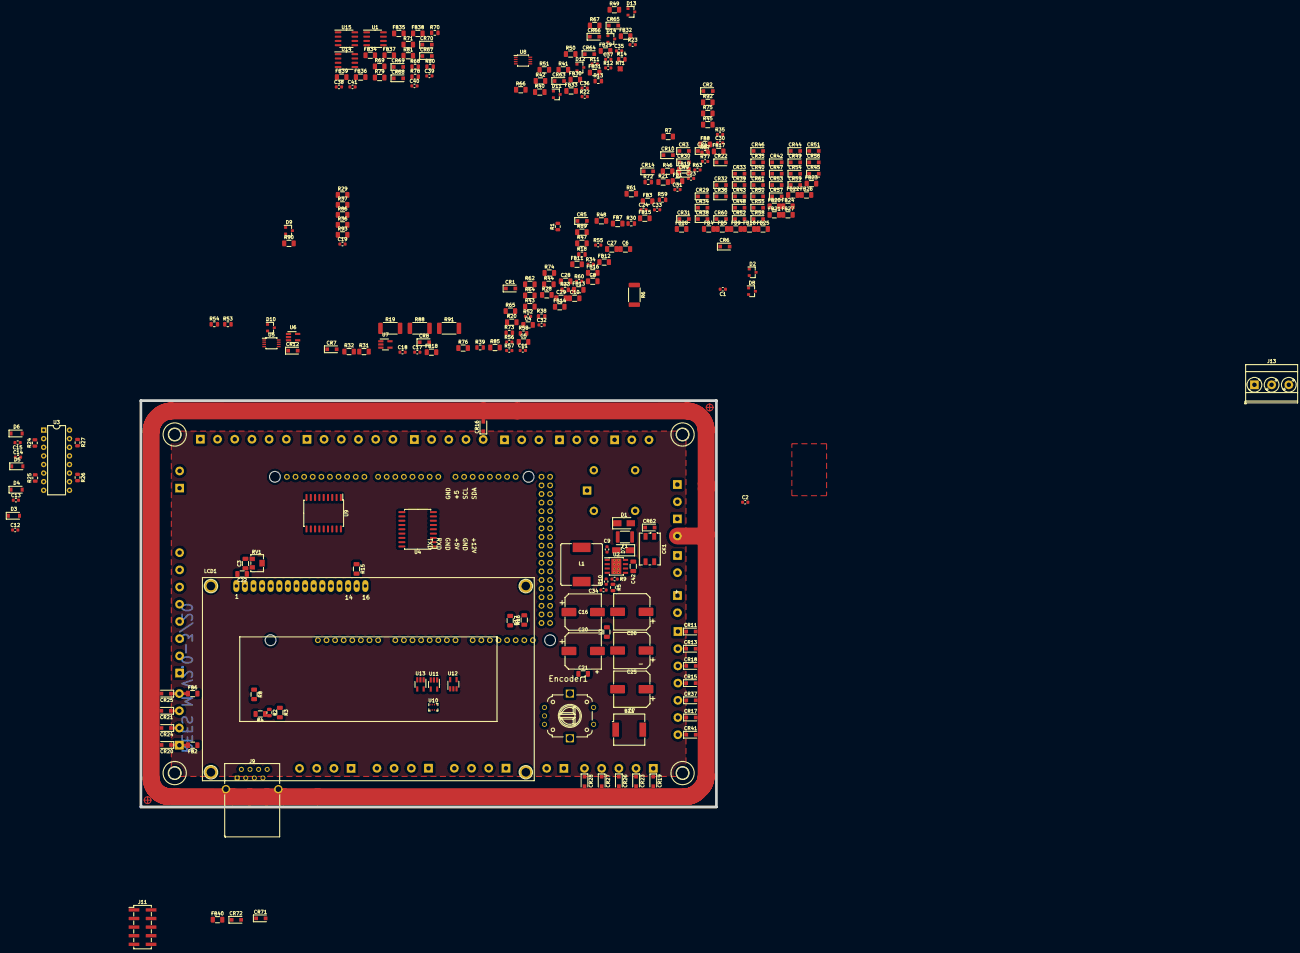
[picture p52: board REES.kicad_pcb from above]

Board: 2 copper layers, 170.0 x 120.0 mm, 310 parts (0 on the bottom side), 209 nets.

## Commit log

2020-04-14 Update electronics/arduino/diagrama_bloques_esquema.md, images/diagrama_bloques_esquema.png, alimentacion_esquema.md, electronics/arduino/alimentacion_esquema.md, electronics/arduino/mcu_esquema.md, 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
2020-04-14 Montaje de la caja en metacrilato
2020-04-14 tapas para distintos tipos de pantallas
2020-04-15 organización de archivos de electrónica
2020-04-15 colocando archivos
    [bmr_000_completo_para_fabricar.igs, bmr_001_carcasa_superior_para_fabricar.igs, bmr_002_tapa_culo_para_fabricar.igs, bmr_003_anillo_culo_para_fabricar_con_reji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]
2020-04-15 PCB files
    [022057038.stp, 022057048.stp, 22057028.stp, EC11_Rotary_Encoder_Switched.step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]
2020-04-16 Planos de corte dxf y planos en Freecad de todas las piezas de metacrilato
    [Balancin.FCStd, Balancin.dxf, Base.dxf, Base_metacrilato.FCStd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]
2020-04-17 Se adjunta la carpeta de archivos stp, se ha corregido la cuna ponindole 4 tornillos para sujetar a la base y se empieza las pruebas de la pala con pivote
    [Balancin.FCStd, Balancin.dxf, Balancin.step, Balancin_v2.FCStd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]
2020-04-18 Manuales de reespirator 2020
2020-04-19 Update electronics/arduino/ARDUINO-ELECTRONICS.md, images/arduino/pinout_mcu.png files
2020-04-21 Update images/arduino/esquema3DB.png, images/arduino/esquema3DF.png files
2020-04-26 Update electronics/arduino/interfaz_esquema.md, images/arduino/encoder.png, images/arduino/interfaz_esquema.png, images/arduino/lcd4x20.png files
2020-04-27 Se adjuntan piezas que faltaban como el acople motor y piezas nuevas en las que se esta trabajando
    [Acople motor.FCStd, Acople_Motor.step, Pala_v2.FCStd, Pala_v3.FCStd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]
2020-05-02 Update electronics/arduino/actuadores_esquema.md, images/arduino/actuadores_esquema.png, images/arduino/actuadores_esquema1.png, images/arduino/actuadores_esquema2.png, images/arduino/actuadores_esqu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
2020-05-02 Update images/arduino/pcb00.png, images/arduino/pcb01.png files
2020-05-04 Versión de Arduino para Reespirator 2020
2020-05-06 Se corregi un error en el archivo de corte de la pieza "Trasera"
    [Montaje.step, Montaje_Caja.FCStd, Montaje_Caja_v2.FCStd, Montaje_caja.step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]
2020-06-09 motor driver
